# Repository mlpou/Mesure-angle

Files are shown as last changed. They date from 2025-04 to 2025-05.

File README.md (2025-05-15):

# Mesure-angle
## Context
FleYe calibration method is aimed to generate a general equation representing the angle formed by a light source and a camera at a variable altitude. The data obtained by applying this data analysis is useful to the [ILLUMINA model](http://obsand.org/wiki/index.php?n=Prof.IllumEn) developed by the professor Martin Aubé. It is used to grasp a better understanding of the impact of light pollution in the environnement. To obtain data, the [FleYe system](http://obsand.org/wiki/index.php?n=Prof.HABLANv3-Raspbian) is attached to a stratospheric balloon. FleYe is a 12 camera positioned to create a half-sphere shape, allowing it to cover and take pictures of the ground for 360 degrees. These flights are done during the night to better detect the light sources. During these flights, FleYe takes photos of the region beneath itself. These photos are then analysed with FleYe calibration method. 

## Material
- iPano RS232" camera mount (its command set is part of the repository (iPano RS232 Command.pdf))
- 3D printed adaptator for the FleYe to fit on the mount ("FleYe-Ipano-adaptator.skp" and "FleYe-Ipano-adaptator.stl")
- Tripod (we used a bonifoto)
- Raspberry pi
- Red LED
- Breadboard

## Procedures
The first step of the calibration is a photo capture. The FleYe has to capture a reference point at different known relative angles. It was decided that the reference point would be fixed, and that the FleYe would move to create those angles. The FleYe was set on the iPano camera mount with our adaptator, wich was placed on the tripod. Our referance point was a red LED that was suspended to the ceiling on a breadboard, but any small source of light could work. It is important that the LED is the only source of light in the room, because otherwise the analysis could be biaised. We recomand a to choose a room with no window and to tape cardboard on the sides of the door. The FleYe was connected to a raspberry pi that would control the photo capture. We took 12 960 pictures, so a SD card or a hard drive is recommended if there is not enough storage on the pi itself. Then, in order to obtain the most reliable result, the LED has to be centered with the FleYe's center camera. In our case, it was camera C on raspberri pi 172.20.4.162. The program `Photo.py` take a picture only with the center camera and transfers it to the raspberry pi. Then, `centuring.py` returns the emplacement of the center of mass of the light from the LED with an array presenting its x and y position. The ideal value would be (2028, 1520) but we accepted a 50 to 75 pixel error on each value. Once it was centered, the program `Control.py` is ready to be lauched. `Control.py` uses the `Ipano.py` serial method developed by Alexandre Simoneau (original repository : https://github.com/alsimoneau/ipano.git) which is based on the command set (iPano RS232 Command.pdf) and converts it into python fonctions. The right port has to be defined when seting the ipano object. It sould will be printed each time the code runs. There also might be some ajustement to make with the paths troughout the whole code. Finally, the amount of pictures to be taken, the angles' precision is controlled and the pause time between the captures is are determined by the input parameters of the `measures` fonction. `altIteration`, the first parameter, determines the number of altitude angles that the mount will take. `altPrecision`, the second parameter, determines the space in degree in between each altitude angle. The mount will distribute evenly the captures on both sides of the zenith. Make sure that the maximum angle that the mount will take (altIteration*altPrecision/2) is lower that 45 degrees, because it is the physical limit of the mount. `azIteration` determines the number of azimuth angles the mount will take for each altitude angle. `pauseTime` determines the pause time take between each set of pictures (we recomand not using a value under 5). The whole capture process will take many hours/days depending on how many pictures will be taken. We used used `measures(90,1,12,5)` for a total of 1080 pictures and we estimated that it took a bit more than 24 hours. All the pictures will be stored in a directory called `data` under the following organisation :

data -> pi's ID -> camera letter

Once the pictures are taken, they have to be analysed. The program  `data_analysis_mc` creates a second degree polynomial regression. The program uses the mass center of the bright pixels as a reference value. We recomand using the mass center, as it is more acurate. The variables `alt`, `precision` and `az` correspond to `alIteration`, `altPrecision` and `azIteration` from `Control.py`. It is important that they corespond. The `analysis` fonction sould be called with each camera's path so that they all get a regression. A text file we be created in the same path. The `polyRelation2` fonction returns coefficients from the polynomial regression between the x and y pixel position of the light and the altitude and latitude angles.
The indexes corespond to the following : 

0. Constant
    
1. x coefficient
    
2. x² coefficient
    
3. y coefficient
    
4. y² coefficient
    
The first array is the altitude's regression and the second is the azimuth's regression. 
The arrays will be stored in a text file name `regression` in each camera's directory. Make sure to delete them before doing another regression.

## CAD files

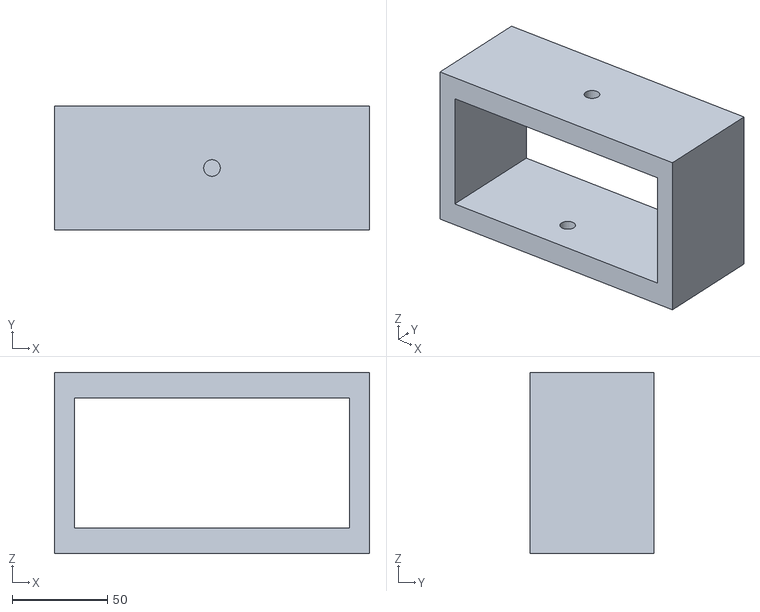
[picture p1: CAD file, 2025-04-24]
FLeYe-Ipano-adaptor.stl
165.0 x 65.0 x 95.0

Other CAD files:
FLeYe-Ipano-adaptor.skp

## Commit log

2024-10-01 Fonction pour la mesure
2024-10-01 Rename Traitement d'image to Analyse des données
2024-10-01 Création de numéro d'image en angle
2024-10-01 Ajustement de la focntion
2024-10-01 Update d'analyse de données
2024-10-08 Test avec les régressions
2024-10-29 Ajustement de la todo
2024-10-29 Add files via upload
    dossier images pour le test de la boucle
2024-11-19 Les deux fichiers sont joints
2025-01-23 Version qui marche, mais à optimiser pour prendre moins de tems
2025-01-23 Ça marche avec les trois pi en parallèle
2025-03-26 ajout de centering
2025-04-03 J'ai enlevé la clef pour publier
2025-04-04 Pour de vrai
2025-04-23 Indices qui suivent les photos
2025-04-24 Tri des photos sans lumière
2025-04-24 model for the adaptator
    [FLeYe-Ipano-adaptor.skp, FLeYe-Ipano-adaptor.stl]
2025-05-15 Changement de readme
